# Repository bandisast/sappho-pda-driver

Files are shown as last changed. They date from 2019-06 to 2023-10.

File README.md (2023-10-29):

# NOTE: As of 2023-10-30, this repository is a public archive. The [Sappho Project has moved from my personal account to a GitHub Organisation](https://github.com/Sappho-Project) and the directories have been split into separate repositories.

# S.AP.P.H.O. Project
## Scattering-based APparatus for Portable Haematological analysis via Optics

### Information
This repository is the main repository for the [SAPPHO project](http://microengineering.iem.ihu.gr/curprojects.html). The design, fabrication, calibration, and testing of a non-invasive, portable Mie scattering-based blood quality sensor are presented in this project. The prototype device currently consists of a 1500x1-pixel photodiode array sensor, a 650 nm laser diode, and a novel case designed to facilitate a variety of optical experiments. Furthermore, this project presents the findings of several in-vivo and in-vitro experiments performed with either the current device or previous prototypes of the device. The SAPPHO project began with our thesis ([Scattering measurements with the Beaglebone microcomputer for portable biomedical sensors](http://microengineering.iem.ihu.gr/repo/2022MichailidouBantis.pdf)\), but its roots can be traced back to the work of [Stratos Gkagkanis](http://microengineering.iem.ihu.gr/repo/2019Gkagkanis.pdf) ([`@StratosGK`](https://github.com/StratosGK)), [Konstantinos Karakostas](http://ikee.lib.auth.gr/record/305140?ln=el) ([`@konkarak`](https://www.linkedin.com/in/konkarak/)), [Ilias Kavoukis](http://microengineering.iem.ihu.gr/repo/2020Kavoukis.pdf) ([`@iliaskavoukis`](https://www.linkedin.com/in/iliaskavoukis/)), and [Dr. Michail E. Kiziroglou](https://spiral.imperial.ac.uk/bitstream/10044/1/48460/4/17_SPIE_asPublished.pdf) ([`@m.kiziroglou`](https://www.imperial.ac.uk/people/m.kiziroglou)).

### Directories
* `./debian-mirror`
  - In case the official Beagleboard website stops distributing the Debian image (`bone-debian-8.7-iot-armhf-2017-03-19-4gb.img.xz`) used in our thesis, this directory contains links to mirrors.
* `./sappho-analysis`
  - The `sappho-analysis` directory contains scripts for analyzing samples taken with the Toshiba TCD1103GFG PDA or the AMS TSL1401CL PDA.
* `./sappho-cad` 
  - This directory houses `.stl` files for the 3D-printed case as well as other peripherals.
* `./sappho-docs`
  - The `sappho-docs` directory contains pdf documents such as our thesis and its presentation, our publications, and the TeX source code for some legal documents required for the project.
* `./sappho-pcb`
  - The directory `sappho-pcb` contains the files required for printing and/or editing the project's PCB 
* `./sappho-pda`
  - This directory contains the source code required for using the Toshiba TCD1103GFG PDA sensor in conjunction with the Beaglebone Black Rev. C microcomputer, as well as some installation scripts. This code has been forked from StratosGK's "SGK_PDA" driver for the AMS TSL1401CL PDA. Please copy this directory under the directory `/home/debian/`.
  
### Installation & Building
#### Beaglebone Black Rev. C
##### Prerequisites
* Edit /etc/systemd/journald.conf (limit the amount of storage used for logging purposes):
  - `SystemMaxUse=16M`
  - `#MaxLevelStore=warning`
  - `#MaxLevelSyslog=warning`
* Edit /boot/uEnv.txt (disable the Universal Cape):
  - `dtb=am335x-boneblack-overlay.dtb`
  - `cmline-coherent_pool=1M net.ifname=0 quiet`
  - `#cape_universal=enable`
* Reboot the Beaglebone microcomputer
  - `sudo reboot`
* Replace the Linux kernel:
  - `cd /opt/scripts/tools/`
  - `git pull`
  - `sudo ./update_kernel.sh --bone-kernel --lts4_4`
* Reboot the Beaglebone microcomputer again

##### Installation
* Clone the repository on the Beaglebone microcomputer
  - `git clone https://github.com/bandisast/sappho-pda-driver.git`
* Execute the installation script:
  - `cd ~/sappho-pda/Tools`
  - `sudo bash fullInstall.sh`
* Compile the C source code
  - `cd ..`
  - `cd Code`
  - `make`

You should now be able to use the driver as such: `./sappho_exec framesCount intgrTime fpsCount`. For example, `./sappho_exec 10 40 50`.

### Future plans
- [ ] Support the Arduino UNO R4
- [ ] Support the Espressif ESP32D
- [ ] Support the Raspberry Pi RP2040
- [ ] Support an STM32 microcontroller

### Current Primary Contributors
* [@bandisast](https://github.com/bandisast)
* [@maro-michailidou](https://github.com/maro-michailidou)

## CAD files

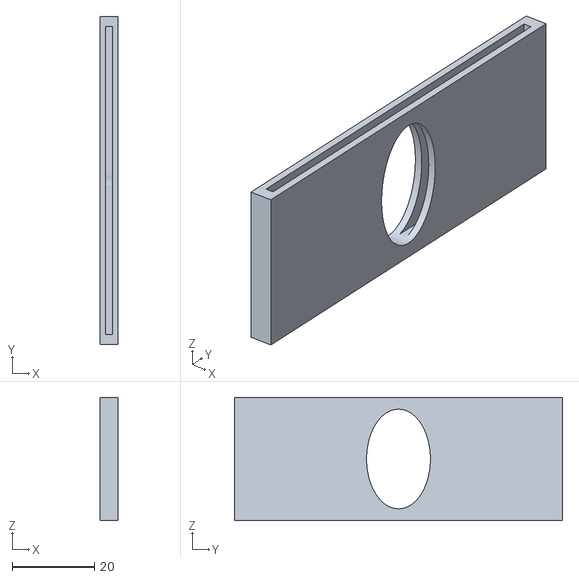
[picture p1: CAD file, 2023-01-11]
sappho-cad/perifereiako-kounoupi.stl
4.50 x 80.0 x 30.0

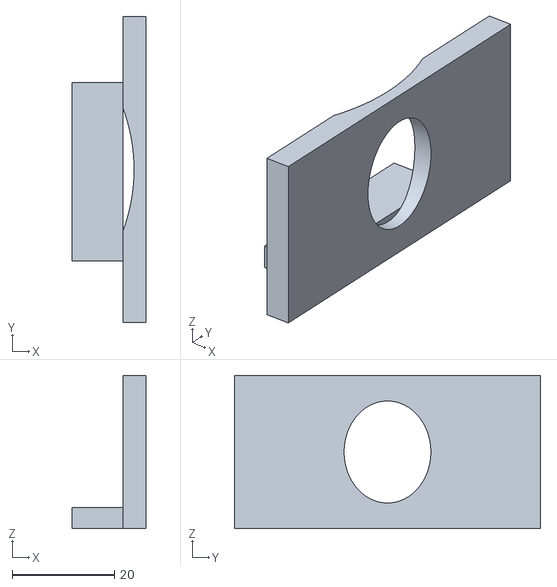
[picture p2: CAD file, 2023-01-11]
sappho-cad/perifereiako-dracula.stl
14.5 x 60.0 x 30.0

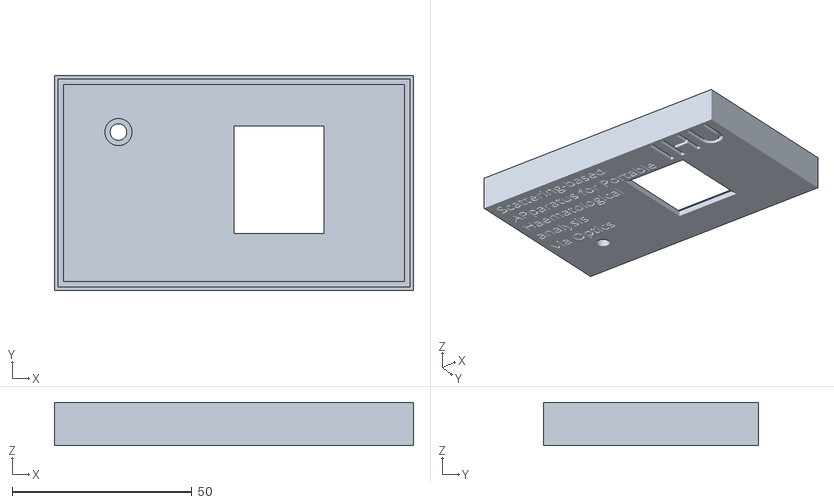
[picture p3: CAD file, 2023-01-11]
sappho-cad/megalo-kapaki-sosto.stl
100.0 x 60.0 x 12.0

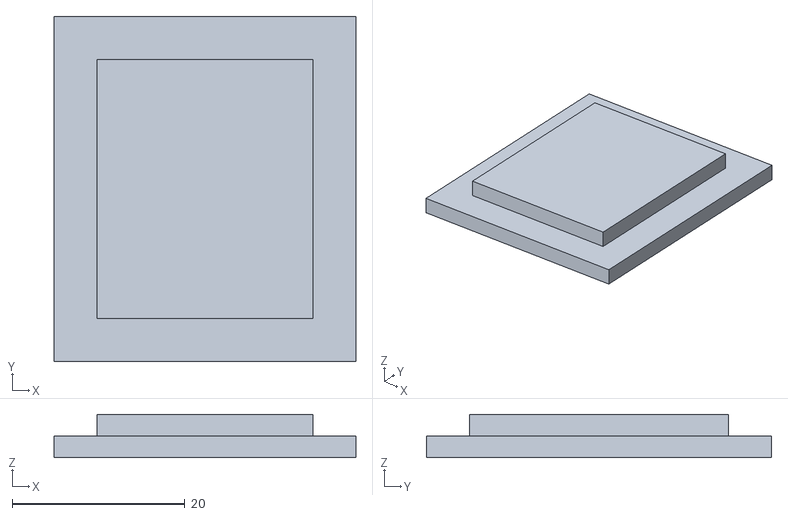
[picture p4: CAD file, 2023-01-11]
sappho-cad/kapaki-mikro.stl
35.0 x 40.0 x 5.00

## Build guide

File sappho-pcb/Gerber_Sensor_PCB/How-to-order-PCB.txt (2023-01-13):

How to Order PCB

Please refer to:
https://docs.easyeda.com/en/PCB/Order-PCB

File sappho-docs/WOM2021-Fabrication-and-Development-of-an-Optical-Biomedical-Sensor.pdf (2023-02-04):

6

# th International Workshop on Microsystems

## Alexander Campus, International Hellenic University, 15 December 2021

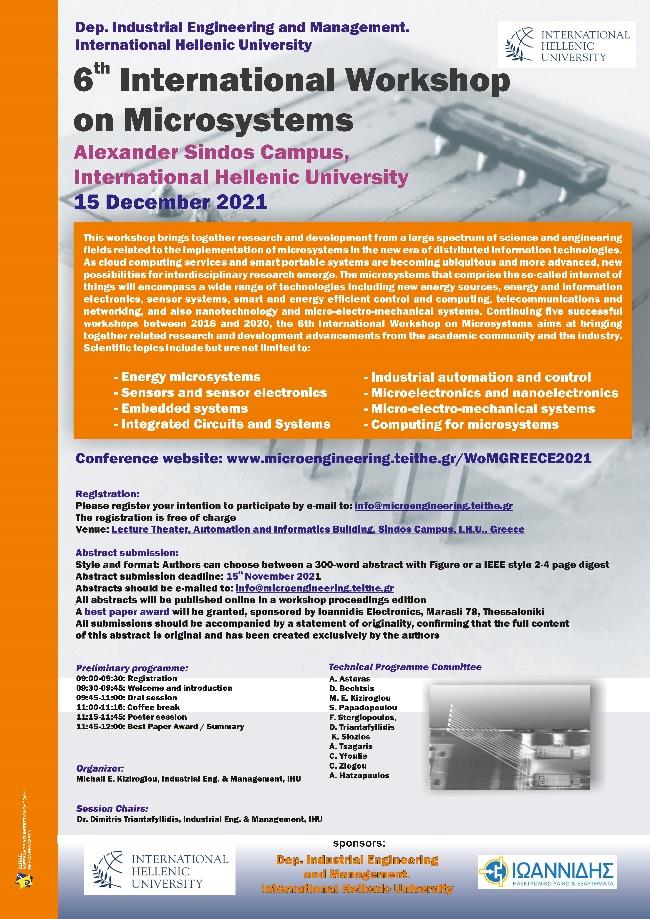
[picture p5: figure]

# Workshop Proceedings

th International Workshop on Microsystems Alexander Campus, International Hellenic University, Thessaloniki, Wednesday 15 December 2021

## Programme

08:45-09:00: Registration
Please check-in or register at the front desk.

09:00-09:15: Welcome and introduction

### 09:15-10:45: First Oral Session (Session Chair: Dr. D. Triantafyllidis, IHU)

09:15 – 10:00: Nanoparticle based sensors. Prof. Dimitris Tsoukalas, Dept. of Physics, National Technical University of Athens 21WOM-01 (keynote, invited).

10:00: Design and Construction of an Automated Milling Machine for producing PCBs. M. Mytilinaios and D. Triantafyllidis, 21WOM-02.

10:15: A python software tool for 2D and 3D image processing, A. Boukogiannis and D. Bechtsis, 21WOM-03.

10:30: Design Framework of a Decision Support System used in a Canning Industry, G. Kokkas, A. Styliadis-Heinz, F. Stergiopoulos and D. Bechtsis, 21WOM-04.

10:45-11:15: Coffee Break and Poster Session

Fabrication and Development of an Optical Biomedical Sensor, A. Bantis, M. Michailidou, E. Gkagkanis, K. Karakostas and M. E. Kiziroglou, 21WOM-05.

### 11:15-12:00: Second Oral Session (Session Chair: Dr. D. Triantafyllidis, IHU)

11:15: A Novel Approach on Fault Detection of Analog and Mixed Signal Circuits by monitoring the fluctuation of the Supply Current, V. D. Vassios, A.T. Hatzopoulos and D. K. Papakostas, 21WOM-06.

11:30: Rectification and boosting circuit for acoustic power transfer, V. Fountas, D. Makarikas, M.
E. Kiziroglou, K. Karakostas and A. Chatzopoulos, 21WOM-07.

11:45: Automation of a Washing Machine: An Open-Source Approach, K. Kostopoulos and D. Triantafyllidis, 21WOM-08.

12:00-12:15: Best Paper Award by Ioannidis Electronics. Concluding remarks.

# Fabrication and Development of an Optical Biomedical Sensor

A. Bantis†1

, M. Michailidou†1
, E. Gkagkanis¹

, K. Karakostas²

,and M. E. Kiziroglou¹

Department of Industrial Engineering & Management, International Hellenic University¹ , Department of
Electronics, Echovista GmbH, United Kingdom²

Abstract—Portable biomedical devices have proven useful during the COVID-19 pandemic, as devices like optical pulse oximeters and rapid detection tests have been readily available to the public. This paper presents a prototype version of a non-invasive, portable, Mie scattering-based blood quality sensor, developed by the authors for their theses.

Index Terms—biomedical sensors, Mie scattering, circuit board, machine learning, embedded systems, optics, data analysis

I. INTRODUCTION
T
HIS paper represents the combined efforts of the four authors throughout multiple years. After a proof of concept was submitted by Karakostas et al[2], a prototype of the apparatus was developed by two of the authors. A second, improved version is currently in development, aiming to upgrade the sensor’s hardware and optics, implement new features, and improve the data analysis using more advanced algorithms, as well as machine learning.

The apparatus uses a light source and a detector for the detection of Mie scattering in blood cells. Mie scattering describes the behaviour of electromagnetic waves when encountering particles larger or equal to 1
10 of the wavelength,
but is most useful for particles with a diameter comparable to the wavelength. Depending on the wavelength of light and the particle’s size and optical properties, a distinct intensity pattern will be identified at different angles of the detector.[1]

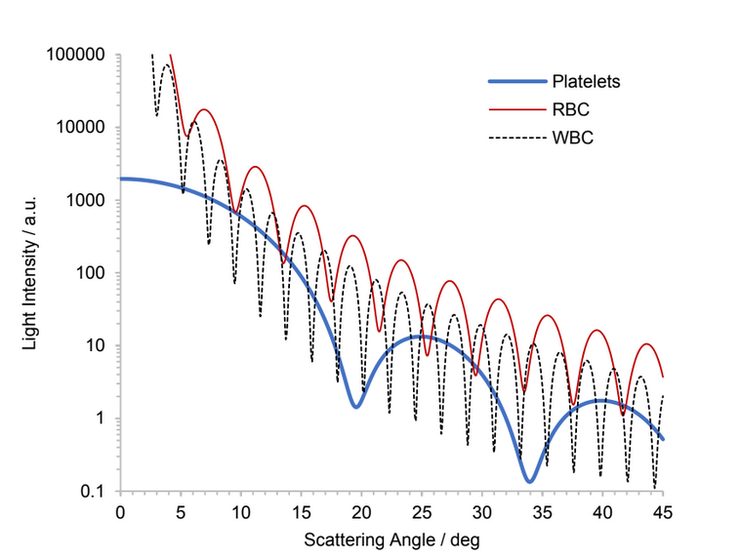
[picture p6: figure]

Figure 1: Mie scattering simulation for different types of blood cells, in Mieplot[2][3]

II. HARDWARE

The prototype was composed of a Beaglebone Black Rev. C microcomputer, a circuit board, a 655nm laser diode, a photodiode array, an RGB LED, a button, and the 3D-printed case. Modifications to the 3D-printed case of the project are crucial to ensure our ability to examine auricular cartilage tissue, as the current housing was designed for in-vitro blood samples in cuvettes and in-vivo finger samples.[1][4] Moreover, the proper cooling of the Beaglebone Black rev. C,

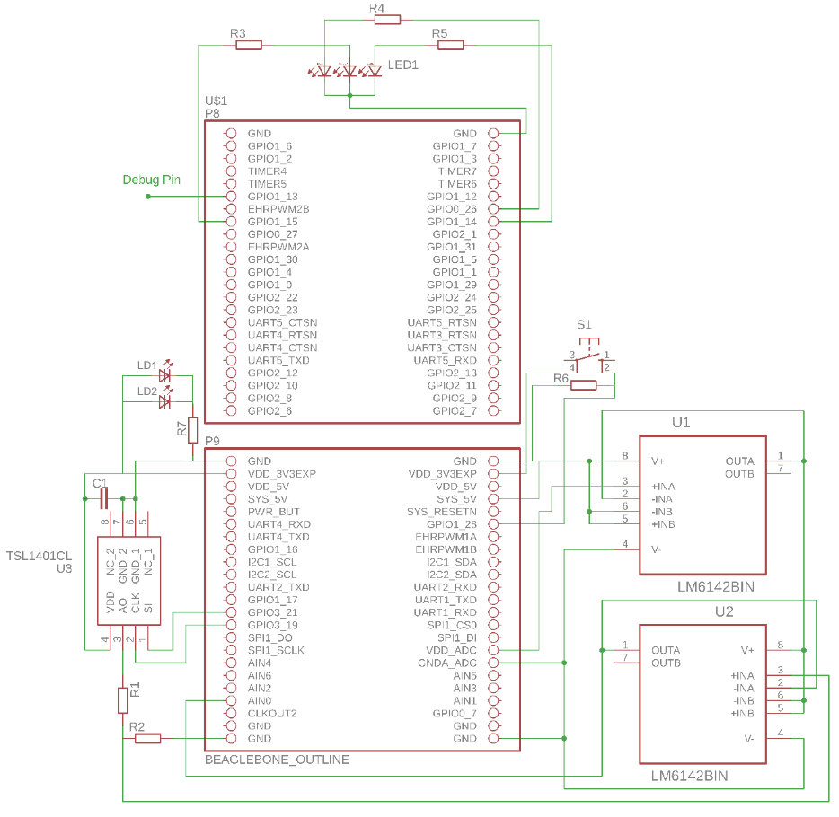
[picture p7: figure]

Figure 2: The circuit diagram of the device[4]

which can reach up to 54.6oC, should be taken into account for the longevity of the device. For this purpose, heat sinks and air vents will be added inside the case. Furthermore, the addition of two optical polarizing filters - one in front of the laser beam and one in front of the PDA - were added to the apparatus for noise reduction and polarizing angle experimentation.

III. OPTICS

A few modifications have been suggested that would make a significant difference to the existing device. The use of two 43mm polarizing lenses is beneficial for the reduction of noise because polarization has been proven advantageous in such configurations, by preventing multiple scattering events from interfering with the resulting data. Another proposed change is the usage of two identical lasers on a beam-merging,

## 6th International Workshop on Microsystems

polarizing configuration i n o rder t o i ncrease t he signal-tonoise ratio of the data. The final proposed change is a threelaser configuration s o a d ichroic fi lter co uld be ad ded to the previously mentioned design along with a waveplate and a laser on a different frequency, allowing the gathering of more information compared to previous designs.[2][3]

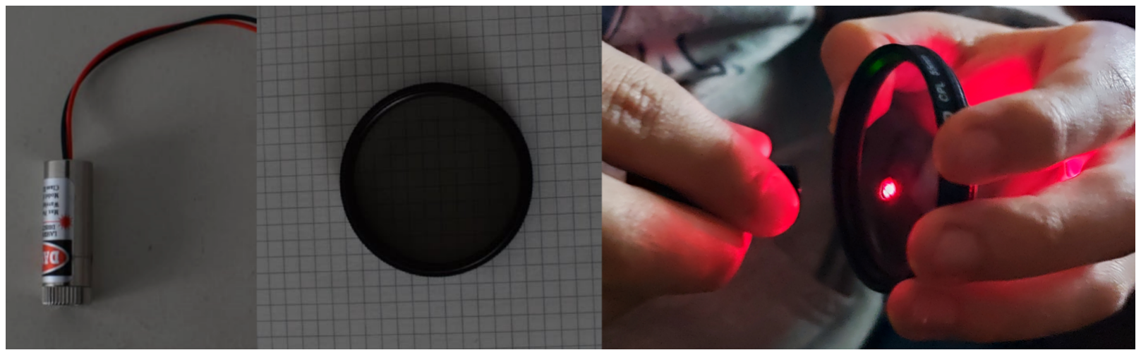
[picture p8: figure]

Figure 3: One of the laser diodes (a), a polarizing lens blocking unpolarized light (b), the lens allowing most of the laser diode’s light through (c)

IV. SOFTWARE

The Beaglebone’s SoC contains an ARM CPU and two programmable real-time units (PRUs). The ARM processor is responsible for handling the system services of Debian GNU/Linux, such as the handling of sample files, the execution of the main program, the initialisation of the PRUs, and memory management. The PRUs are responsible for driving the photodiode array (PDA) and creating interrupts (PRU0), or for handling the Analog-to-Digital Converter and storing the sensor’s data (PRU1). Frame-capturing cycles are divided into three parts, the first of which is integration. During the integration time, the PDA is operated normally but any samples are ignored. Secondly, during the sampling period, the PDA is operated normally and its samples are collected. Lastly, a delaying phase is executed, during which the PRUs do not execute operations, to keep the number of sampling cycles per second equal to the number requested by the user. This process is repeated until the end of the measurement, when the number of recorded frames matches the number requested by the user.[4]

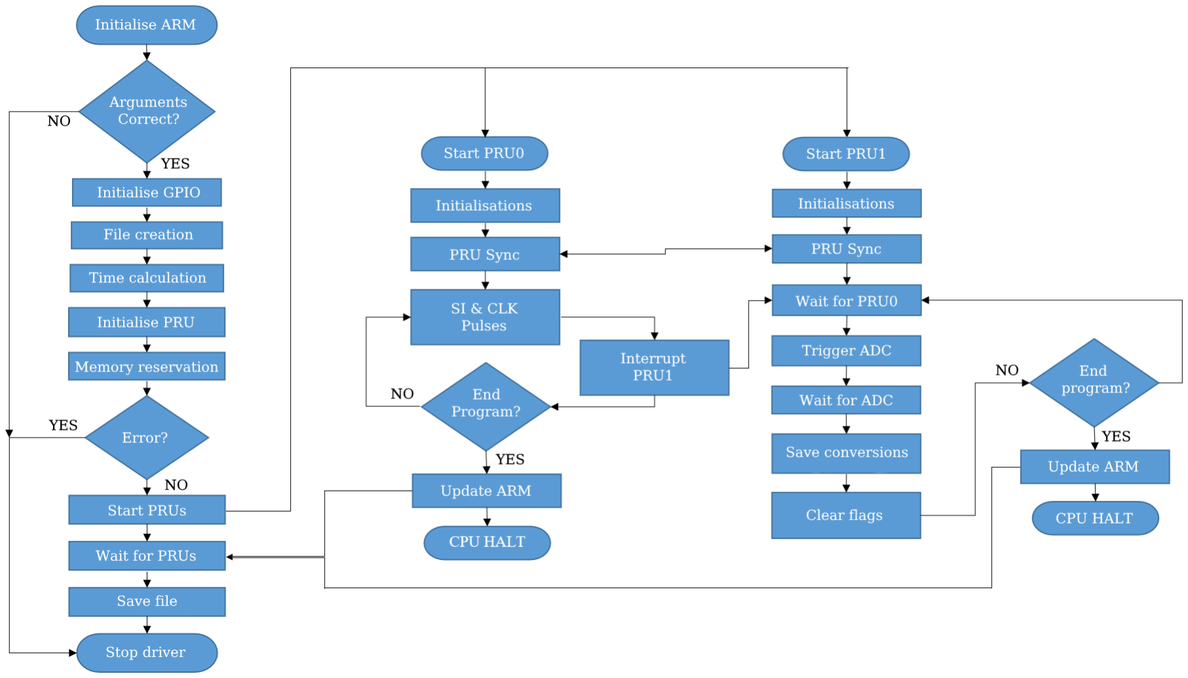
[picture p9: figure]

Figure 4: A flow diagram of the software driver[4]

V. DATA ANALYSIS & MACHINE LEARNING

Since the apparatus currently only records and stores raw data, an external device is required for data analysis. Any personal computer capable of executing C++, Python, and Matlab programs can be used for this purpose. The first programs, developed in Matlab, would execute simple algorithms to determine the accuracy and repeatability of the sensor and would analyse the sample to ascertain the concentration of the particles, the size of the particles, and (for in-vivo samples) the heart rate of the subject. One such program would also draw the Mie plot of the average sample with its expected plot. New programs are currently in development in C++ and Python, implementing more complex algorithms in order to improve the quality of the results and the time efficiency of the process. One such example is programming a good approximation of the model in order to acquire more information about the size, number, and type of particles in the liquid sample.

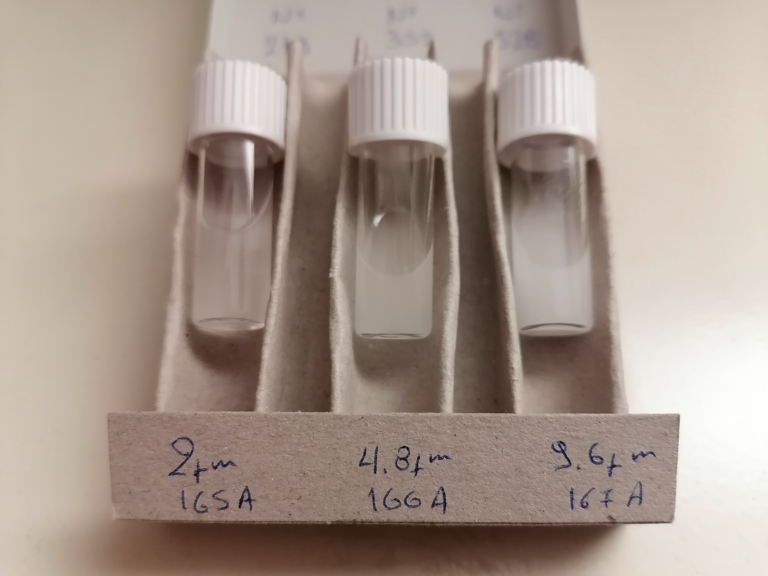
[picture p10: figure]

Figure 5: Cuvettes with latex spheres, used for the calibration of the sensor

Assuming a scanning frequency of 50 frames per second and a duration of 5 seconds, the 128-pixel sensor will return a sample of 32000 12-bit unsigned integers every time the code is executed. It is unlikely that a human could adequately recognise patterns between several samples of this size and type. Therefore, machine learning is also being considered as a means to analyse the sensor’s data. The training dataset will be voluntarily provided by individuals at a microbiological laboratory, where their anonymous samples will be paired with the results of their blood test. A first draft of the multilayer neural network is currently under development in Python. The authors are also looking into unsupervised machine learning algorithms, such as the K-means algorithm, in order to discover any unknown underlying patterns.[5]

REFERENCES

[1] Karakostas K., ”Portable system development for Mie scattering analysis, to determine the size of blood cells in in-vivo and in-vitro studies”, Aristotle University of Thessaloniki, 2019
[2] Konstantinos Karakostas, Stratos Gkagkanis, Korina Katsaliaki, Peter Kollensperger, Alkiviadis Hatzopoulos, and Michail E. Kiziroglou, ¨ ”Portable optical blood scattering sensor”, Microelectronic Engineering 217 (2019) 111129, Elsevier
[3] C. Iosifidis, K. Katsaliaki, P. Kollensperger and M. E. Kiziroglou, ”Design of an embedded sensor system for measuring laser scattering on blood cells”, Bio-MEMS and Medical Microdevices III, SPIE Vol. 10247 102470G-1
[4] Gkagkanis E., ”Fabrication of a photo-diode sensor apparatus with the Beaglebone microcomputer for use in non-invasive biomedical sensors”, Alexander Technological Educational Institute of Thessaloniki, 2019
[5] Simon Haykin, ”Neural Networks and Learning Machines”, McMaster University, Hamilton, Ontario, Canada

## 6th International Workshop on Microsystems

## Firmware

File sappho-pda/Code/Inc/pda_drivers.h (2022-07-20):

/*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
*****************************************************
*                                                   *
* Adapted for the S,AP.P.H.O PDA project by:        *
* Bantis Asterios (@bandisast), AutomE, 2022        *
*                                                   *
****************************************************/

#include <stdio.h>
#include <stdint.h>
#include <math.h>
#include <string.h>
#include <stdlib.h>
#include <dirent.h>
#include <unistd.h>
#include <prussdrv.h>
#include <pruss_intc_mapping.h>

/***************/
/* Definitions */
/***************/
#define ARGUMENTS_NUM (4)
#define PRU0 0
#define PRU1 1

#define ErrorSecondsSleep (2)	//How many seconds will the LED stay Red.

/* PDA */
#define PIXELS 			(1500)
#define MIN_INTGR_TIME	(10)
#define MAX_INTGR_TIME	(10000)

/* CALCULATION MACROS */
#define EXTRA_PULSE				(14) // 14 extra pulses are required at the end
#define EXTRA_WAIT_B4_NEXT_SI	(10) // 20us exta time between integrations
#define uS_TO_S					(0.000001) // conversion from us to s
#define S_TO_uS					(1000000)
#define INSTRUCTION_DELAY		(0.00000001) // Minimum delay time for a delay loop
#define FIRST_32_PULSES			(32) // The first 32 setup clock pulses
#define KHZ_TO_MHZ				(1000)

/* PATHS */
#define PRU0_BIN_PATH "/home/debian/sappho-pda/Code/PRU/PRU0.bin"
#define PRU1_BIN_PATH "/home/debian/sappho-pda/Code/PRU/PRU1.bin"

/* Return Codes
unsigned int (32bit, big endian, 0 ~ 4.294.967.295) */
#define NO_ERR			0
#define ARGU_ERR 		100000	//Incorrect number of arguments.
#define	CLK_ERR 		100001	//Clock frequency out of bounds.
#define INTGR_ERR 		100002	//Integration time out of bounds.
#define FILE_ERR 		100003	//Error while opening the data file.
#define PRU_INIT_ERR 	100004	//Failed to initialize PRU.
#define PRU_DEINIT_ERR 	100005	//Failed to de initialize PRU.
#define PRU_START_ERR 	100006	//Failed to start PRUs.
#define PRU_EVENT_ERR	100007
#define CALC_ERR		100008
#define MEM_ERR			100009	//Not enough RAM for the requested samples.
#define FOLDER_ERR		100010	//"Samples" folder not found in the directory.
#define GPIO_ERR		100011
#define BUTTON_ERR		100012
#define LED_ERR			100013


/* RAM Offset */
#define Pixels_Offset				0
#define Frames_Offset				1
#define Integr_Time              	2
#define Handshake0_Offset			3
#define ExtraTime_Offset            4
#define Handshake1_Offset			5
#define DDR_Addr_Offset				6
#define DDR_Size_Offset				7

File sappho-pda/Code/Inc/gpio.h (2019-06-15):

/****************************************************
*                                                   *
*---------------------------------------------------*
*  PDA Drivers                                      *
*---------------------------------------------------*
*                                                   *
* Copyright (C) 2019, Gkagkanis Efstratios,         *
*    				all rights reserved.            *
*                                                   *
* Redistribution and use in source and binary forms,*
* with or without modification, are permitted       *
* provided that the following condition is met:     *
*                                                   *
* 1. Redistributions of source code must retain the *
* the above copyright notice, this condition and    *
* the following disclaimer.                         *
*                                                   *
*                                                   *
* This software is provided by the copyright holder *
* and any warranties related to this software       *
* are DISCLAIMED.                                   *
* The copyright owner or contributors be NOT LIABLE *
* for any damages caused by use of this software.   *
*                                                   *
****************************************************/

#include "pda_drivers.h"

/*************/
/* Variables */
/*************/
typedef enum rgb_led_t{
	OFF = 0,
	RED,
	GREEN,
	BLUE,
}rgb_led_t;

extern uint32_t Init_GPIO(void);
extern uint32_t Button_Wait_To_Press(void);
extern uint32_t Button_Wait_To_Release(void);
extern uint32_t Write_LED(rgb_led_t rgb_led);

/**********/
/* MACROS */
/**********/

/* PATHS */
#define EXPORT_PATH			"/sys/class/gpio/export"

#define DIRECTION_BUTTON	"/sys/class/gpio/gpio60/direction"
#define DIRECTION_LED_R		"/sys/class/gpio/gpio26/direction"
#define DIRECTION_LED_G		"/sys/class/gpio/gpio47/direction"
#define DIRECTION_LED_B		"/sys/class/gpio/gpio46/direction"

#define VALUE_BUTTON		"/sys/class/gpio/gpio60/value"
#define VALUE_LED_R			"/sys/class/gpio/gpio26/value"
#define VALUE_LED_G			"/sys/class/gpio/gpio47/value"
#define VALUE_LED_B			"/sys/class/gpio/gpio46/value"

/* BUTTON FUNCTIONALITY */
#define BUTTON_PRESSED "1"
#define BUTTON_RELEASED "0"

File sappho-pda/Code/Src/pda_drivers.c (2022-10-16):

/*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
*****************************************************
*                                                   *
* Adapted for the S,AP.P.H.O PDA project by:        *
* Bantis Asterios (@bandisast), AutomE, 2022        *
*                                                   *
****************************************************/


#include "pda_drivers.h"
#include "sample_file.h"
#include "debug.h"
#include "gpio.h"

/**********/
/* MACROS */
/**********/
#define RED_TIME 5 /* Turn on RED LED for 5 seconds in case of error */

/************************/
/* Variable Definitions */
/************************/
uint32_t *pru_shared_ram = 0;	//Int pointer for RAM addressing.
uint16_t *ddr_casted = 0;
uint32_t sample_len;

double clkfreq;
uint16_t frames;
double intgr_time;
double fps;

uint16_t intgr_delay;
uint32_t extra_time;
uint16_t prog_total_cycles = 3099; //number of CLK pulses/frame, without the extra time delay (2 * 1500 pixels + 2 * 32 dummy outputs + 2* 14 dummy outputs + 7 CLK pulses for the ICG stage)

/*************************/
/* Function Declarations */
/*************************/	
static uint32_t Argv_Handler(int *argc, char *argv[]);
static uint32_t Delay_Calculation(void);
static uint32_t Mem_Alloc(void);
static uint32_t Init_PRUSS(void);
static uint32_t Start_PRUs(void);
static void Wait_For_PRUs(void);
static uint32_t Deinit_PRU(void);

int main(int argc, char *argv[])
{
	uint32_t result, file_number;
		
	#if DEBUG_MODE == 1
		printf("Debug Mode ON\n");
	#endif
	
	result = Argv_Handler(&argc, argv);
	Debug_Print("Argv_Handler result:", &result);
	if (result != NO_ERR) goto exit;
	
	result = Init_GPIO();
	Debug_Print("Init_GPIO result:", &result);
	if (result != NO_ERR) goto exit;
	
	result = Write_LED(BLUE);
	Debug_Print("Write_LED result:", &result);
	if (result != NO_ERR) goto exit;
	
	result = Button_Wait_To_Press();
	Debug_Print("Button_Wait_To_Press result:", &result);
	if (result != NO_ERR) goto exit;

	result = Write_LED(GREEN);
	Debug_Print("Write_LED result:", &result);
	if (result != NO_ERR) goto exit;
	
	result = Create_File();
	Debug_Print("Make_File result:", &result);
	if (result != NO_ERR) goto exit;
	
	result = Delay_Calculation();
	Debug_Print("Delay_Calculation result:", &result);
	if (result != NO_ERR) goto exit;
	
	result = Init_PRUSS();
	Debug_Print("Init_PRUSS result:", &result);
	if (result != NO_ERR) goto exit;
	
	result = Mem_Alloc();
	Debug_Print("Mem_Alloc result:", &result);
	if (result != NO_ERR) goto exit;
	
	result = Start_PRUs();
	Debug_Print("Start_PRUs result:", &result);
	if (result != NO_ERR) goto exit;
	
	Wait_For_PRUs();
	
	file_number = Save_Samples();
	Debug_Print("Save_Samples result:", &file_number);
	if (file_number >= ARGU_ERR) goto exit;
	
	result = Deinit_PRU();
	Debug_Print("Deinit_PRU result:", &result);
	if (result != NO_ERR) goto exit;
	
	result = Write_LED(OFF);
	Debug_Print("Write_LED result:", &result);
	if (result != NO_ERR) goto exit;

	result = Button_Wait_To_Release();
	Debug_Print("Button_Wait_To_Release result:", &result);
	if (result != NO_ERR) goto exit;
	
	return file_number;
	
exit:
	Debug_Print("Error code:", &result);
	Write_LED(RED);
	sleep(RED_TIME);
	Write_LED(OFF);
	return result;
}

/********************/
/* HELPER FUNCTIONS */
/********************/

static uint32_t Argv_Handler(int *argc, char *argv[])
{
	uint32_t result = ARGU_ERR;
	
	if (*argc != ARGUMENTS_NUM) {
		printf("Incorrect arguments.\n");
		printf("Example: ./sappho_exec 10 120 50\n");
		printf("First argument: Number of Frames \n");
		printf("Second argument: Integration Time in us. Min = 10 us, Max = 10 ms \n");
		printf("Third argument: Frames per second (fps). Min = 1 fps. Max = 161 fps \n");
		printf("Please try again.\n");
		goto exit;
	}
	
	clkfreq = 500;
	frames = abs(atoi(argv[1]));
	frames++; //The first frame always contains junk data, so we skip it. Therefore, we add an extra frame here for parity. :)
	intgr_time = abs(atof(argv[2]));
	fps = abs(atof(argv[3]));
	
	if(intgr_time < MIN_INTGR_TIME || intgr_time > MAX_INTGR_TIME) {
		goto exit;
	}
	
	result = NO_ERR;

	if (fps >= (int) (S_TO_uS/prog_total_cycles/(1000/clkfreq)) || fps < 1)
	{
		fps = (int) (S_TO_uS/prog_total_cycles);
		printf("Warning: Invalid fps argument; Fps automatically set to its maximum value.\n");
	}
exit:
	return result;
}

static uint32_t Delay_Calculation(void)
{
	intgr_delay=(int) intgr_time*(clkfreq/1000);  //Kinda useless when your clock is 1000 KHz but keeping this here in case the clock frequency changes again
	extra_time = ((S_TO_uS/fps) - (KHZ_TO_MHZ*prog_total_cycles)/clkfreq)*(clkfreq/1000); // ^--- I should play the lottery next time; now the clock frequency is 500 KHz 
	return NO_ERR;
}

static uint32_t Init_PRUSS(void)
{
	uint32_t result = PRU_INIT_ERR;
	int res;
	
	res = prussdrv_init();
	res |= prussdrv_open (PRU_EVTOUT_0);
	res |= prussdrv_open (PRU_EVTOUT_1);
	if (res != 0) goto exit;
	
	/* PRU Interrupt Setup */
	tpruss_intc_initdata pruss_intc_initdata = PRUSS_INTC_INITDATA;
	result = (uint32_t) prussdrv_pruintc_init(&pruss_intc_initdata);
	if (result != 0) goto exit;
	
	result = NO_ERR;
exit:
	return result;
}

static uint32_t Mem_Alloc(void)
{
	uint32_t result = MEM_ERR;
	void *pru_shared_ram_void;
	void *ddr_ram_void;
	uint32_t ddr_address;
	
	/* PRU Shared RAM & DDR Setup */
	prussdrv_map_prumem(PRUSS0_SHARED_DATARAM, &pru_shared_ram_void);
	pru_shared_ram = (uint32_t *) pru_shared_ram_void;
	prussdrv_map_extmem((void **) &ddr_ram_void);
	ddr_address = prussdrv_get_phys_addr((void *) ddr_ram_void);
	
	sample_len = (PIXELS * frames * sizeof(frames));
	if (sample_len > prussdrv_extmem_size()) {
		goto exit; /*If DDR memory allocated to PRUs is not enough, terminate. */
	}
	
	pru_shared_ram[Pixels_Offset] = PIXELS;
	pru_shared_ram[Frames_Offset] = frames;
	pru_shared_ram[ExtraTime_Offset] = extra_time;
	pru_shared_ram[DDR_Addr_Offset] = ddr_address; 
	pru_shared_ram[DDR_Size_Offset] = sample_len;
	pru_shared_ram[Integr_Time] = intgr_delay;


	//CLEAR MEMORY
	ddr_casted = (uint16_t *) ddr_ram_void;
	memset(ddr_casted, 0x00, (sample_len+1));
	
	result = NO_ERR;
exit:
	return result;
}

static uint32_t Start_PRUs(void)
{
	uint32_t result = PRU_START_ERR;
	int res;
	
	pru_shared_ram[Handshake0_Offset] = 0;
	pru_shared_ram[Handshake1_Offset] = 0;

	res = prussdrv_exec_program (PRU0, PRU0_BIN_PATH);
	res |= prussdrv_exec_program (PRU1, PRU1_BIN_PATH);
	if (res != 0) goto exit;
	
	while(pru_shared_ram[Handshake0_Offset] != 22522);	//PRU0 Handshake through pru_shared_ram

	prussdrv_pru_wait_event(PRU_EVTOUT_1);	//PRU1 Handshake through INTC
	prussdrv_pru_clear_event (PRU_EVTOUT_1, PRU1_ARM_INTERRUPT);
	if (res != 0) goto exit;
	pru_shared_ram[Handshake0_Offset] = 111;
	pru_shared_ram[Handshake1_Offset] = 222;
	
	result = NO_ERR;
exit:
	return result;
}

static void Wait_For_PRUs(void)
{
	while(pru_shared_ram[Handshake0_Offset] != 55255);	//Wait for PRU0 to finish.

	//printf("PRU0 handshake sent\n");
	prussdrv_pru_wait_event(PRU_EVTOUT_1);	//Wait for PRU1 to finish.
	//printf("PRU1 handshake sent\n");
	prussdrv_pru_clear_event (PRU_EVTOUT_1, PRU1_ARM_INTERRUPT);
	//printf("PRU clear event sent\n");
}

static uint32_t Deinit_PRU(void)
{
	uint32_t result;
	int res;
	
	res = prussdrv_pru_disable(PRU0);
	res |= prussdrv_pru_disable(PRU1);
	res |= prussdrv_exit ();
	
	if (res == 0) {
		result = NO_ERR;
	}
	else {
		result = PRU_DEINIT_ERR;
	}

	return result;
}

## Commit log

2019-06-15 Created a README.md inside the Samples folder
2022-05-01 PRU0 reworking - Draft of SH/ICG sync part
    The first draft of the PRU0 rewriting. This includes the "annoying", and not particularly loopable part of the code.
    Untested, as I do not have the driving circuit working yet.
2022-05-03 Device tree experimentation
    I hate device trees. Enough said.
2022-05-15 inverted the clock in case the timing diagram implies it due to the NOT gates
2022-05-16 timing PDA as an electronic camera shutter
2022-06-27 Add ICG pin
2022-07-30 Cleanup / First frame junk data fix
    It is done. My preciousss.
2022-07-31 Added an Octave script for analysing samples
2022-08-04 Bug fix: frame duration is now correct, rather than double
2023-01-10 Add files via upload
    1-layer PCB is for a cost effective shield for the BBB that checks functionality of the sensor etc.
    6-layer PCB is the same shield for the BBB but one that conforms to the EU Technical File.
    Sensor PCB is the PCB that holds the TCD1103GFG in place.
2023-01-11 Put Maro's CAD/PCB/Doc files in separate directories
    [kapaki-mikro.stl, megalo-kapaki-sosto.stl, perifereiako-dracula.stl, perifereiako-kounoupi.stl]
2023-01-11 Test how unzipping the pcb files affects the linguist
    [Drill_PTH_Through.DRL, Drill_PTH_Through_Via.DRL, Gerber_BoardOutlineLayer.GKO, Gerber_BottomLayer.GBL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]
2023-02-08 Add SGK sensor analysis code
